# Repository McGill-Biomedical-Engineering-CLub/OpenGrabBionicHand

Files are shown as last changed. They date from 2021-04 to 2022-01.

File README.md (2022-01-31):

# OpenGrabBionicHand
### Date Launched: June 3, 2020
### Date Delivered: September 1, 2020
# Electronic Hardware System
## Circuit Schematic


### Parts Used:
* Arduino Pro Mini: Used to control all other electronics in the device. Receives analog input from the emg sensor and outputs commands to the servo shield and lcd screen via i2c communication. Datasheet: https://components101.com/microcontrollers/arduino-pro-mini
* FT231X: Provides the Arduino with serial communication from a USB port connected to the laptop. Datasheet: https://www.sparkfun.com/products/13263
* Gravity EMG Muscle Sensor: Measures the EMG signal at the patient's muscle and outputs a 10 bit ADC signal (range of 0-1023) to the analog pin A0 of the Arduino UNO. The device consists of 2 modules: The electrode module, containing 3 dry electrodes, is strapped to the user's muscle, and the signal processing module, which performs basic differential signal processing and interfaces with the analog pin. Datasheet: https://wiki.dfrobot.com/Analog_EMG_Sensor_by_OYMotion_SKU_SEN0240
* Servo Controller (PCA 9685): 16-channel servo controller. Receives power input from the external power supply and control input from the Arduino via I2C interface. Can control up to 16 servos using PWM signals (pulse with modulation). 
Datasheet: https://cdn-learn.adafruit.com/downloads/pdf/16-channel-pwm-servo-driver.pdf
* LCD Screen (SSD 1306): 0.96" 126x64 OLED screen. Displays to the patient calibration instructions. Communicates with the Arduino via I2C interface. Datasheet: https://components101.com/oled-display-ssd1306
* Rotational Servos (HS-65MG): 6V servo motor with 3 input pins (VCC, GND, PWM). Controlled by the servo controller. Datasheet: https://www.robotshop.com/en/hs-65mg-metal-gear-feather-micro-servo-motor.html
* Power Supply: 7.4V Rechargable LiPo Battery (2200 mAh). Datasheet: https://abra-electronics.com/batteries-holders/batteries-polymer-lithium-ion/prt-11856-polymer-lithium-ion-battery-2200mah-74v-prt-11856.html
### Soldering:
The modules for this circuit are connected on a 5x7cm soldering board. Both sides of the board are utilized to place the components. 


### Current Consumption
Non-Motor Components: (From Datasheets)
|Component |  Idle | Operational | Source of Measurement |  
| ------------- | ------------- | ------------- | ------------- |
|Arduino Pro Mini 5V | 3.1mA | 19.9mA | http://www.home-automation-community.com/arduino-low-power-how-to-run-atmega328p-for-a-year-on-coin-cell-battery/#:~:text=Using%20an%20Arduino%20Pro%20Mini,%2C%20in%20power%2Ddown%20sleep. |
| Gravity EMG Sensor | 0.5mA | 0.5 mA | Measured manually using INA219 current sensor |
| OLED Screen | 1.5mA | 4 mA | Measured manually using INA219 current sensor |
| Servo Controller | 2.2mA | 40mA | Datasheet: https://cdn-shop.adafruit.com/datasheets/PCA9685.pdf |
|**Total**|7.3mA |64.4mA| | 

Adding Motor Consumption

Using an INA 219 current sensor, the current consumed by the motors is measured. This measurement is done on 3 different states of the arm: Idle Open, Idle Closed, and a continous alternation between both states. With a known battery capacity of 2200mAh, the battery life can be calculated.

| Hand State |	Average Motor Current Consumption (mA)	| Average Total Current Consumption (mA)	| Estimated Battery Operating Time (hr) |
| ------------- | ------------- | ------------- | ------------- |
| Idle Open |	41	| 106	| 20.75 |
| Idle Closed	| 181	| 246	| 8.94 |
| Alternating	| 456	| **521**	| **4.22** |

Motor Current Consumption Profile


* It is important to note that only motor current consumption was measured and consumption by other modules are not taken into consideration for this measurement, as the motors are the main source of current drainage. 
# Software System
## Dependency Graph (Internal Modules Only)

### Modules involved:
* Bionic_Arm_Controller (main file): Controls the arm (receives EMG input and outputs signals to servo motors) by calling functions from other modules. 
* Arm_Settings: Contains all dynamic parameters that the user can change in the code.
* Arm_Calibration: Runs the calibration for the arm. Collects samples from both resting and active states of the muscle and determines the signal threshold needed to separate between open and closed hand states. 
* Arm_Servo: Handles the direct control of the servos and allows other modules depending on it to call simple methods such as 'open finger' and 'close finger'
* Arm_Demo: Uses functions from the Arm_Servo library to execute a pre-determined set of maneuvers with the arm.
* Arm_Screen: Handles display commands to the OLED screen.
* Arm_Sampler: Collects an EMG sample from the analog pin. Performs all signal analysis. Evaluates samples and outputs an open/close or error command.  
## Errors and Alerts: 
* Electrode Misplacement Error: The dry electrode is not firmly attached to its position which results in readings that are much higher than the normal range. This error is printed to the screen and persists until the electrode position is adjusted to a valid one. 
## Signal Processing:

Unlike that of the Myoware sensor, the signal obtained from the analog reading of the Gravity EMG sensor is raw. The hardware only uses differential denoising to remove the common noise among the electrodes. Thus, the need for software-based signal processing arises.
 
Example of Raw Signal

raw

Differentiating a contraction from the resting phase visually in this noisy signal is still possible. However, there must be a systematic way that the software can use to easily distinguish between both phases. Hence, a variety of techniques must be used:
1. Establishing a zero baseline: The raw signal has a resting-phase baseline that ranges between 280 and 350 units of amplitude (1 unit = 5V/1024). During calibration, the average value of this baseline is determined. Upon each subsequent reading, the absolute value of the difference between the raw reading and the baseline is calculated to obtain a 'normalized' signal reading.
2. Moving Average Filter: To obtain more smoothing of the signal and to mitigate the effect of sudden noisy spikes in measurements, a moving average filter of window width 8 is used. The filter was implemented internally (no use of external libraries) and by trial-and-error, the mentioned window width was found to be most convenient in terms of signal quality and memory usage. 
3. Multiplying factor: At the end, the processed signal readings are multiplied by a certain factor to make different readings more distinguishable from each other. A factor of 2 was chosen. It is worth mentioning that squaring the readings was an option that was considered; however, this method was found to require double the amount of memory, as it causes overflows in the 16 bit integers used to store the datapoints. 
4. Sampling Rate: The sampling rate also has an impact on the quality of the output signal. A rate of 50Hz is found to be convenient. 

Note: Frequency domain-based signal processing is not applicable to this iteration, as it requires a significant amount of memory. The Arduino Pro Mini total RAM memory is only 2048 Bytes, of which most are used for calibration and the LCD screen. 

Example of Processed Signal

final_sig

As seen in the figure above, clear peaks can be identified in the signal, with each peak corresponding to a muscle contraction.

## Calibration 
The function CalibrateDry is used mainly for this iteration. It is found in the Arm_Calibration.cpp file. 
### Determining the baseline
Before starting calibration, a baseline must be established in order to proceed with sampling. The user is instructed to relax and 100 EMG samples are taken at a rate of 100Hz. The average of those 100 samples is the obtained baseline. This value is then to be verified by the checkBelow function which tests the baseline value and ensures that 30 consecutive readings resting values lie below 50. If that is not the case, then the function responsible for updating the baseline is called again and the new baseline is validated. This process repeats until a valid baseline is obtained and tested. 
### Algorithm for Finding the Threshold Value
The same algorithm used from Iteration 1 (Advanced Calibration) is used to find the threshold value that sets apart the resting state from the contracting state. The only changes done are the following: 
* The control system for this iteration does not require 2 threshold values (high and low). Hence, only 1 threshold value to to be determined by the algorithm. 
* The new signal processing technique is used. All samples are obtained using the simpleSample function, as opposed to the first iteration where samples are directly obtained from AnalogRead. 
### Skip Calibration option
Because the full calibration process takes over 1 minute, the user has the option of skipping most of it. This option limits calibration to only establishing the baseline for each channel and assumes a default threshold of 12. With this option calibration would take around 3 seconds for 1 channel and 6 seconds for 2 channels.
## Sample Analysis and Control
The user is allowed to pre-select the number of EMG channels used to control the arm (1 or 2) by modifying the Arm_Settings.h file.
### 1 Channel Input
The control system used for this iteration consists of a toggle switch that is triggered by values above the threshold. Whenever 2 consecutive values are detected above the threshold value, the switch is activated and the state of the hand is changed. In other words, if the hand is open, the first contraction will cause it to close and the second contraction will cause it to open back again. Both contractions must be separated by a buffer refractory time of 800ms.  
The Arm_Sampler library also contains the tools used to judge whether the arm should be open or closed based on the obtained reading. The function evaluateSample returns an integer of either 0, 1, or 2 which correspond to the following:

0 -->Stay in the previous state

1 -->Change state (open if closed and close if open)

2 --> Electrode Misplacement Error (does not change state)

The following flow chart summarizes the control scheme for single channel input control:



### 2 Channel Input
The arm sampler first processes the incoming signal from each channel separately. Upon obtaining the 2 datapoints, the signal from the first (main) channel is evaluated. If a peak is detected, then the hand will immediately be ordered to the open position if closed, and to the close position if in any other position. This is similar to what occurs in 1-channel input control.
If no peak is detected from the first channel, then the device 'listens' to the processed input from the second channel. If a peak is detected from the second channel, then a 3rd 'special' position is performed by the hand. If no peak is detected from either channel, the hand remains in its previous state.
The function evaluateSample2Electrodes handles control for the 2 channel input option. The function returns the following possible outputs:

0 -->Stay in the previous state

1 -->Change state (open if closed and close if in other position)

2 --> Electrode Misplacement Error (does not change state)

3 --> Perform special movement

The following flow chart summarizes the control scheme for 2 channel input control:



# Testing
## Preliminary Testing
Testing was done on 3 usage cycles (calibrate-operate-reset). The primary electrode was placed on the biceps muscle whereas the secondary electrode was placed on the Brachio Radialis muscle.
Testing with PLA skin: 
| Test | Round 1 | Round 2| Round 3 |
| ------------- | ------------- | ------------- | ------------- | 
| Resting Hand False Positives |    0   | 0  | 0 |
| Moving Elbow False Positives |   0 |   0|  0|
| Tapping Hand False Positives |    1  |   2 |1  |
| 10 Contractions | 10/10 |  10/10 | 10/10 |
| 10 Special Movement | 10/10 | 10 /10 | 10/10 |
| 10 Contractions with hold | 10/10 | 10/10  | 10/10 |
| Glass Cup Test (small glass)| 10/10|  10/10 | 10/10 |
| Glass Cup Test (large glass)| 0/10|  0/10 | 0/10 |
| Apple Test | 5/10 | 6/10 | 8/10 |
Testing with Rubber Skin
| Test | Round 1 | Round 2| Round 3 |
| ------------- | ------------- | ------------- | ------------- | 
| Resting Hand False Positives |    0   | 0  | 0 |
| Moving Elbow False Positives |   1 |   0|  0|
| Tapping Hand False Positives |    1  |   1 |1  |
| 10 Contractions | 10/10 |  10/10 | 10/10 |
| 10 Special Movement | 10/10 | 10 /10 | 10/10 |
| 10 Contractions with hold | 10/10 | 10/10  | 10/10 |
| Glass Cup Test (small glass)| 10/10|  10/10 | 10/10 |
| Glass Cup Test (large glass)| 9/10|  10/10 | 10/10 |
| Apple Test | 10/10 | 10/10 | 10/10 |
### Test Protocol Details
Prior to each test: Install the Gravity EMG electrode on the Flexor Carpi Radialis Muscle location. Start the hand and calibrate it.

Resting Hand False Positives: Remain at rest for 1 minute. Report the number of movements initiated from false positive readings.

Moving Elbow False Positives: Similar procedure to Resting Hand False Positive Test. This test involves continously rotating the elbow slowly and reporting any false positives that occur within a minute.

Tapping Hand False Positives: Similar procedure to Resting Hand False Positive. This test involves gently tapping the hand at locations ~3cm away from the electrode in a continous manner and reporting false positives within a minute. 

10 Contractions: Perform 10 distinct contractions using the Flexor Carpi Radialis Muscle, once every 10 seconds. Report the number of successful hand movement responses to the muscle contractions.

10 Special Movements: Before starting the device, add a second electrode on the Biceps Radii Muscle and change the electrode number setting to 2 in the settings.h file. Perform 10 distinct contractions using the Biceps Radii Muscle, once every 10 seconds. Report the number of successful special hand movement responses to the muscle contractions.

10 Contractions with hold: Same protocol as the 10 Contractions test. Leave 30 seconds between 2 successive contractions. 

Glass Cup Tests: Use the hand to pick up an empty glass cup, move it along a distance of 50cm, then lay it down at a specific target point. A glass cup weighing ~200g is used for the small glass and a cup weighing ~500g is used for the large glass. Perform this task 10 times and record the number of successful attempts.

Apple Test: Use the hand to pick up an average size McIntosh Apple, move it along a horizontal distance of 50cm, then place it down on a target location. Perform this task 10 times and record the number of successful attempts.

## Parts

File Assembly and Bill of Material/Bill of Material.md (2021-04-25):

# Bill of Material
| Item | Quantity | Unit |Cost per unit ($CAD)| Cost ($CAD)|Notes
| ------------- | ------------- | ------------- | ------------- | ------------- | ------------- | 
|3D printing Filament for PLA|	1|	per kg|	32.00|	32.00	|All the 3D components are included here.|
|7.4V Rechargable LiPo Battery| 	1|	each|	20.00|	20.00|	
|Wires ||||4.00|	Sufficently large quantities of soldering wire.|
|Soldering Board|	1|	each|	0.40|	0.40||	
|Arduino Pro Mini	|1|	each|	5.00|	5.00||
|USB interface for Arduino mini (FT231X)|	1|	each|	13.00|	13.00|	|
|LCD Monochrome 0.96” OLED Display (SSD1306)|	1|each|	7.00|	7.00||
|HS-65MG Servo Motor	|5	|each	|27.00	|135.00	||
|Servo Controller (PCA 9685)|	1|	each|	16.00|	16.00||	
|SEN0240 Gravity: Analog EMG Sensor	|2	|each	|75.00	|150.00|	Maximal estimate.|
|M3 nuts|1	|pack of 25	|1.50	|1.50	|
|M3 Brass Heat Inserts (4.90mmx4mm)|	1|	pack of 10|	1.10|	1.10||	
|M3x15mm screws	|1|	pack of 10|	2.00|	2.00	||
|M3x4mm screws	|1	|pack of 10	|2.00	|2.00	||
|M3x5mm screws	|1	|pack of 10	|2.00	|2.00	||
|5.25mm ID Shaft Retention Bushing Lock	|5|	each|	1.10|	5.50	|ID: Internal diameter. Must be larger than servo horn diameter(>5mm)|
|Fishing Line (>20 lbs)	|1	|300m-450m of wire	|20.00	|20.00|	Spool quantity to the discretion of the buyer.|
|**Total**	 |||||	 	 **384.50**	 ||

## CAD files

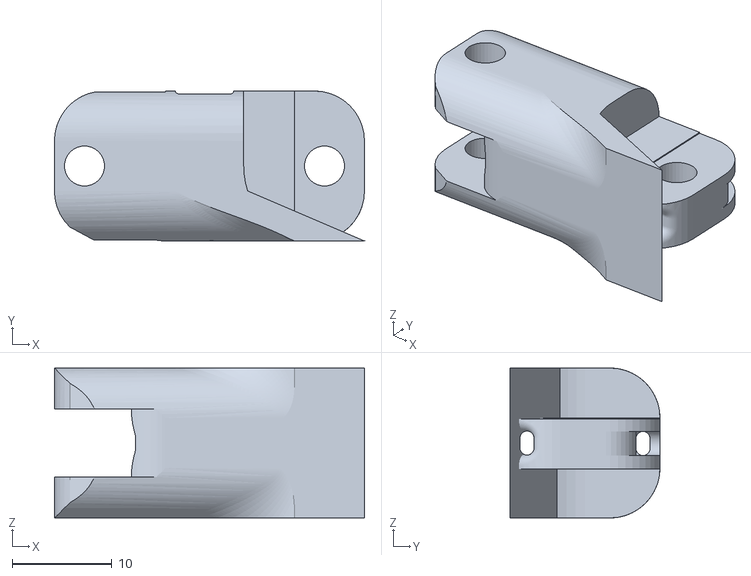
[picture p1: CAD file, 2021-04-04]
3D Print Files/Pinkie finger 3.3 Proximal (Zip).STL
31.0 x 15.0 x 15.0

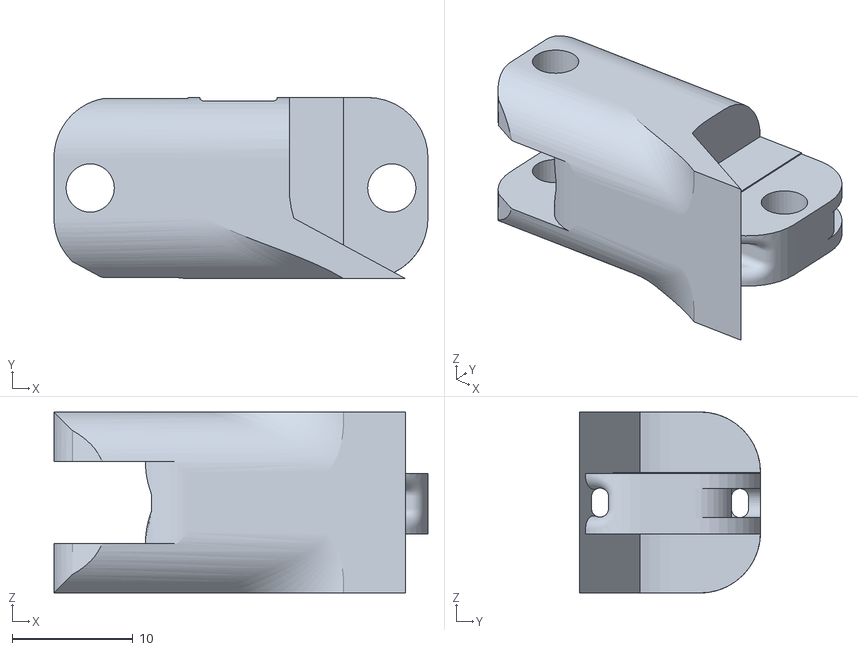
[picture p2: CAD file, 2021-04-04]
3D Print Files/Pinkie finger 3.3 Middle (Zip).STL
31.0 x 15.0 x 15.0

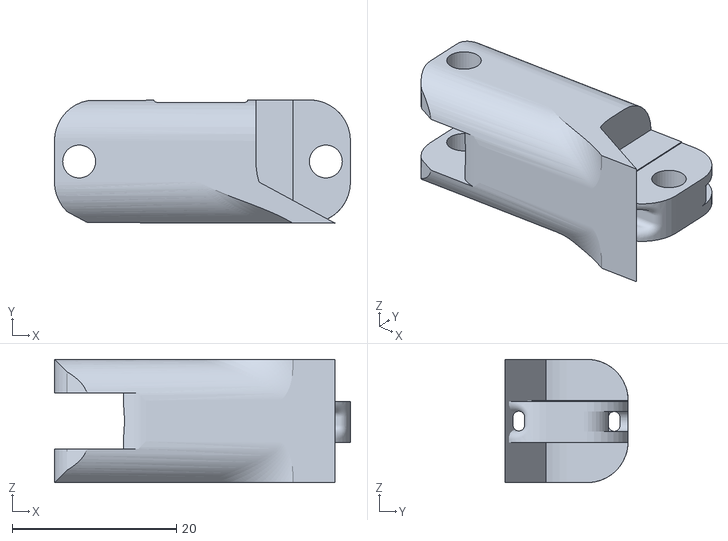
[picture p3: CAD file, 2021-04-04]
3D Print Files/Index-Ring finger Middle 3.3 (Zip).STL
36.0 x 15.0 x 15.0

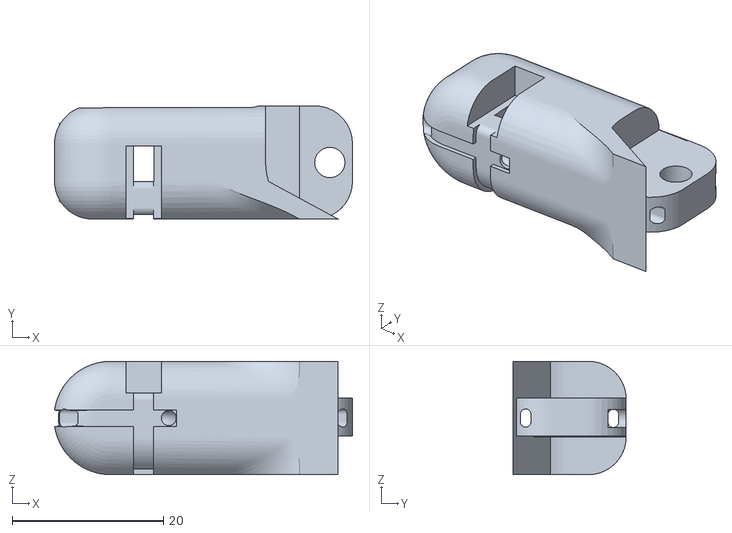
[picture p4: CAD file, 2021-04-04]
3D Print Files/Index-Ring finger Distal 3.4 (Zip).STL
39.4 x 15.0 x 15.0

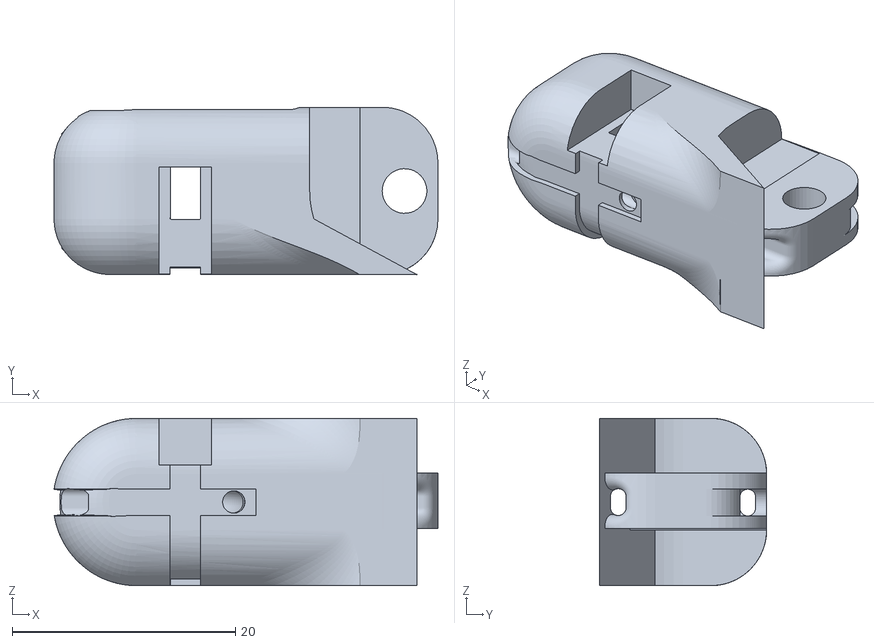
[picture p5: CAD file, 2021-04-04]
3D Print Files/Pinkie finger 3.4 Distal (Zip).STL
34.4 x 15.0 x 15.0

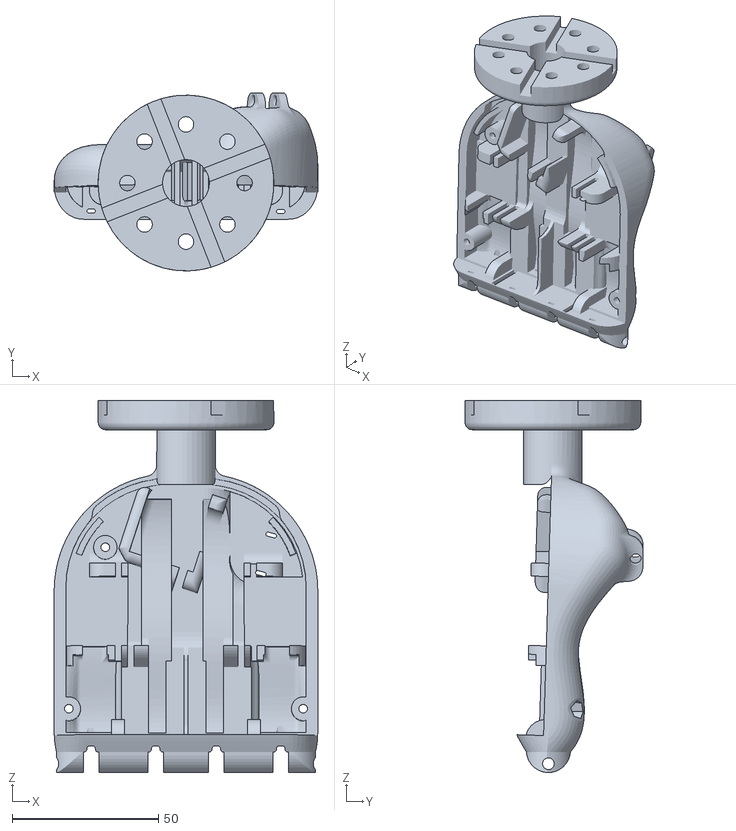
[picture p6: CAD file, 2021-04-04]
3D Print Files/Frontal Palm 1.8(HS-65mg+mg90s thumb).STL
90.0 x 60.7 x 127.0

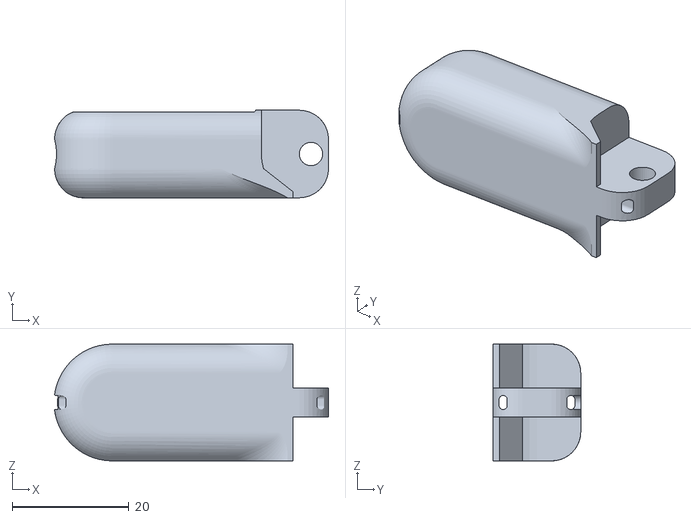
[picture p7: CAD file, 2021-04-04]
3D Print Files/Thumb finger 3.5 (Zip)- distal.STL
46.9 x 15.0 x 20.0

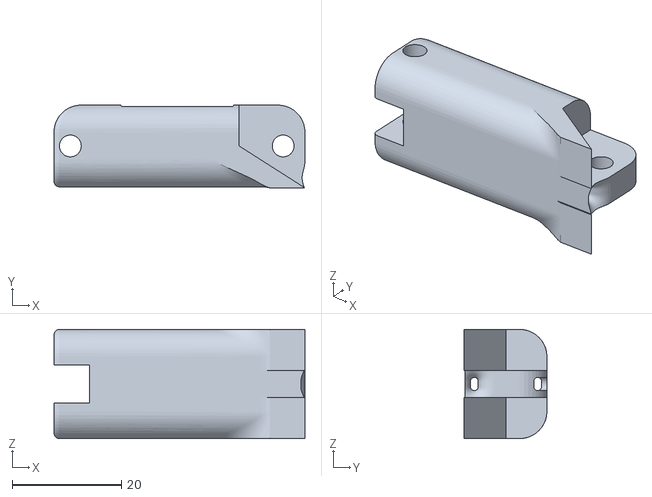
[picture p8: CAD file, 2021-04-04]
3D Print Files/Thumb finger 3.5 (Zip)- proximal.STL
46.0 x 15.2 x 20.0

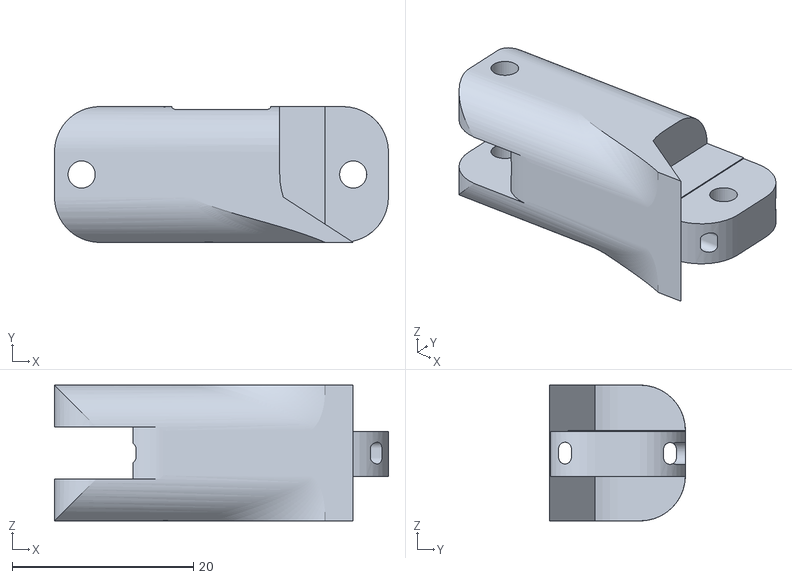
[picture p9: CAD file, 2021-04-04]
3D Print Files/Middle finger 3.4 Middle.STL
36.9 x 15.0 x 15.0

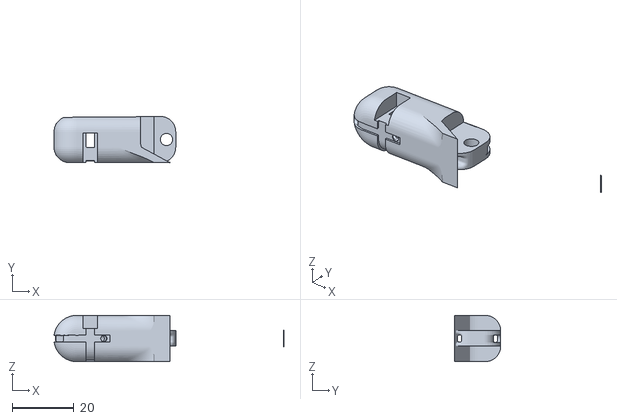
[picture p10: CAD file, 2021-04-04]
3D Print Files/Middle finger 3.4 Distal(Zip).STL
74.5 x 15.0 x 15.0

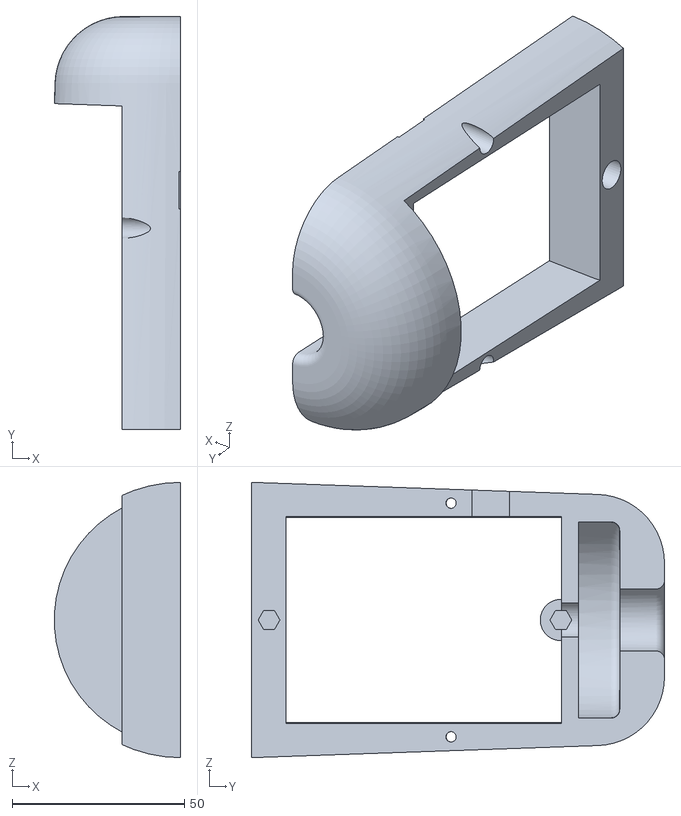
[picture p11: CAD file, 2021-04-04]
3D Print Files/Forearm 3.5-Dorsal forearm.STL
36.6 x 120.0 x 80.0

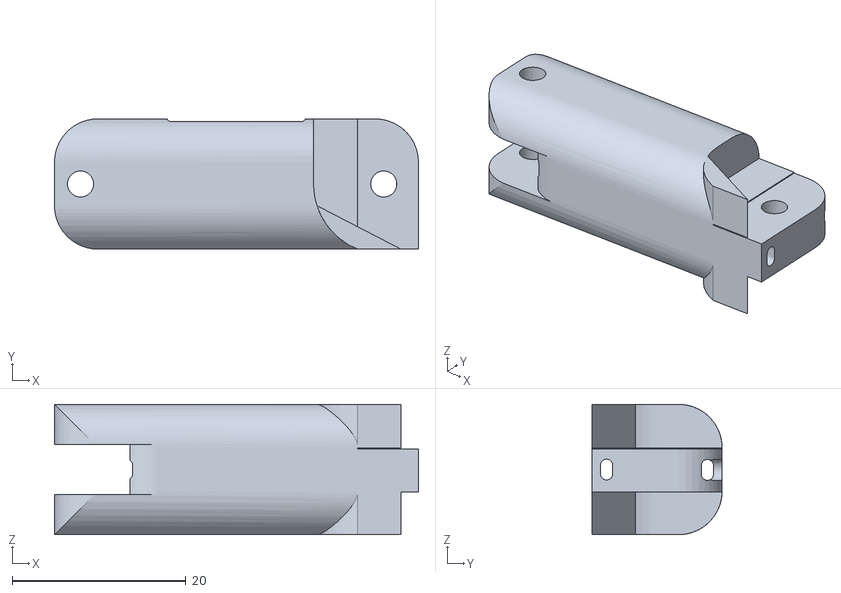
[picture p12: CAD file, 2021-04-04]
3D Print Files/Middle finger 3.4 Proximal.STL
41.9 x 15.0 x 15.0

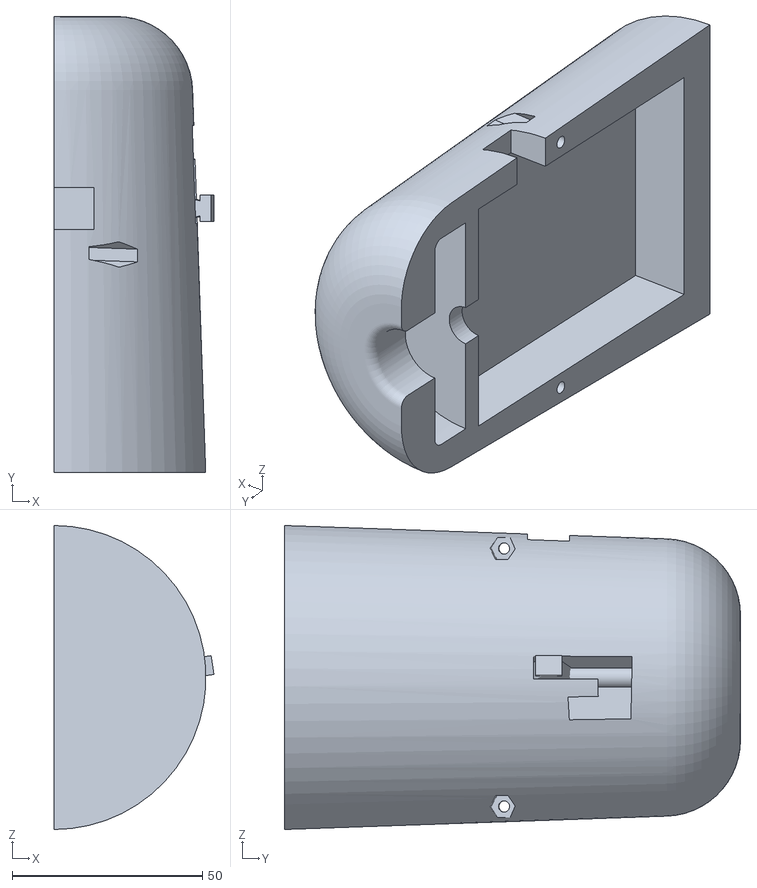
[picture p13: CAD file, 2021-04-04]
3D Print Files/Forearm 3.5- Palmar forearm.STL
42.1 x 120.0 x 80.0

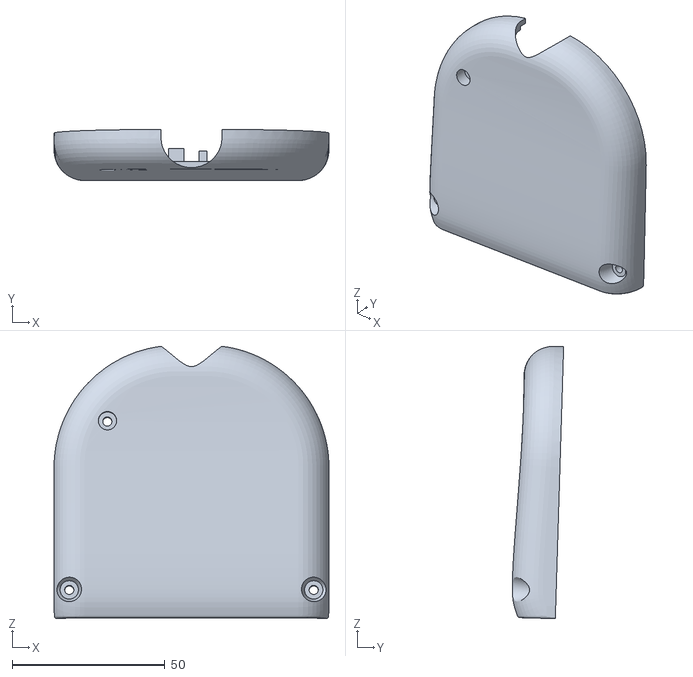
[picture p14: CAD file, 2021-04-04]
3D Print Files/Dorsal Palm 1.8(HS-65mg+mg90s thumb).STL
90.0 x 16.8 x 89.2

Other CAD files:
3D Print Files/Index-Ring finger Proximal 3.3 (Zip).STL
3D Print Files/3mm nail.STL
3D Print Files/Forearm 3.5-Electronics Cover.STL
3D Print Files/3mm palm nail.STL
3D Print Files/Screw Spool 2.4.2 (18mm).STL

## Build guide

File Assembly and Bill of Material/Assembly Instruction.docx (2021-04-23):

Item No. | Part Name | Description | Qty.
1 | Frontal Palm | | 1
2 | Dorsal Palm | | 1
3 | Forearm Dorsal | Includes a non-removable locking mechanism | 1
4 | Forearm Frontal | | 1
5 | Forearm Electronic Cover | | 1
6 | Hitec HS-65MG Servo Motor | | 5
7 | Phalange Pinkie Distal | | 1
8 | Phalange Pinkie Medial | | 1
9 | Phalange Pinkie Proximal | | 1
10 | Phalange Middle Distal | | 1
11 | Phalange Middle Medial | | 1
12 | Phalange Middle Proximal | | 1
13 | Phalange Index/Ring Distal | Index and ring finger share the same dimensions | 2
14 | Phalange Index/Ring Medial | | 2
15 | Phalange Index/Ring Proximal | | 2
16 | Phalange Thumb Distal | | 1
17 | Phalange Thumb Proximal | | 1
18 | Palm Dowel | | 1
19 | Finger Dowel | | 9
20 | Thumb Dowel | The thumb-palm connecting dowel is a Finger Dowel | 1
21 | Spool | | 5
22 | Servo Horn Retention Bushing Lock | | 5
23 | M3x4mm Screw | | 5
24 | M3x5mm Screw | | 5
25 | M3x15mm Screw | | 7
26 | M3 Nut | | 7
27 | M3x5mm Brass Insert | | 5
28 | M3 Allen key | | 1
29 | Fishing line (~50-70cm of length) | | 5

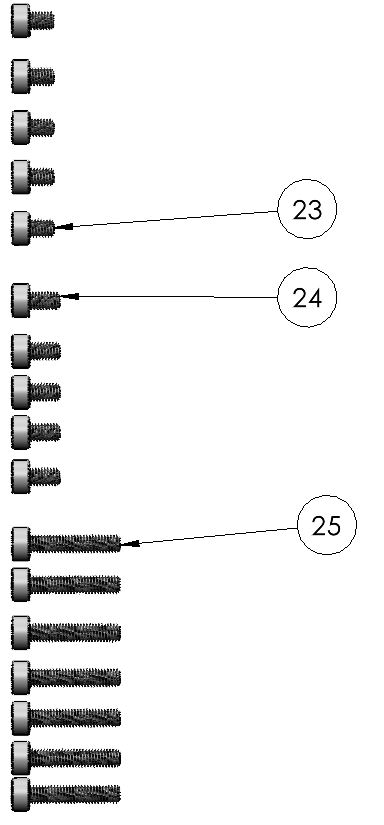
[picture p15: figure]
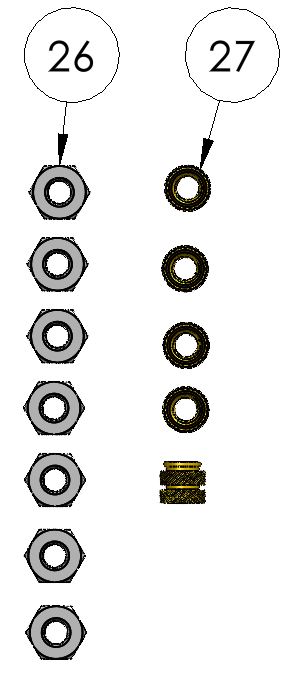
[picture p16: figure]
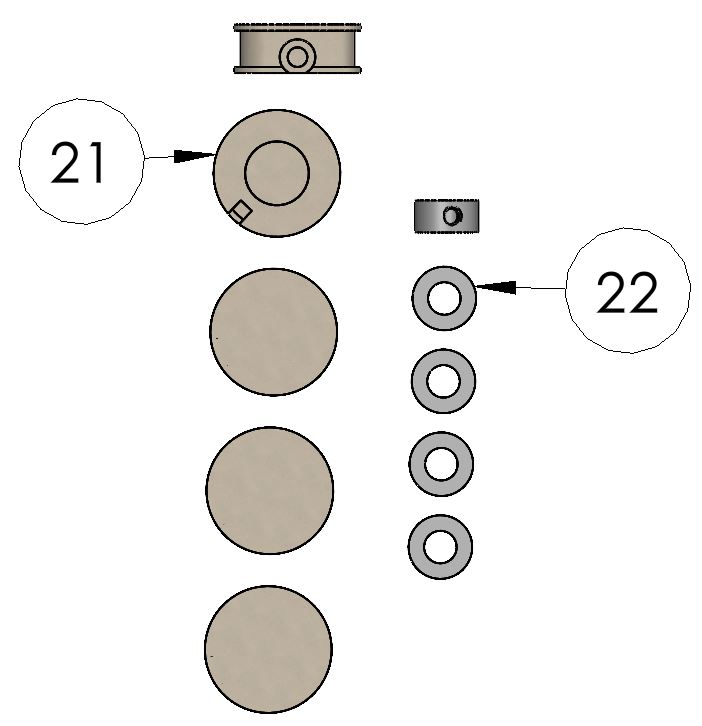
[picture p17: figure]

Assembly Steps

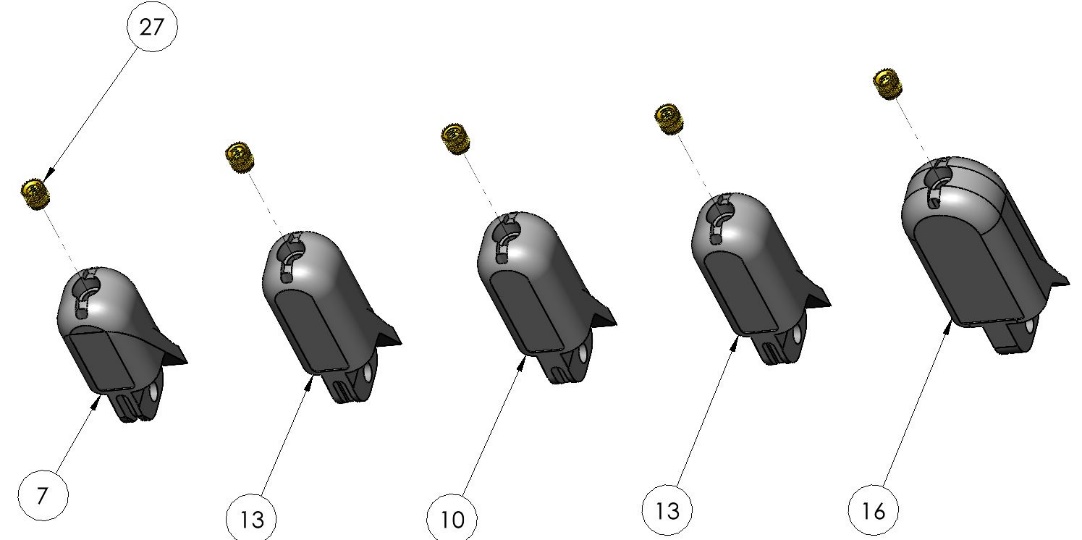
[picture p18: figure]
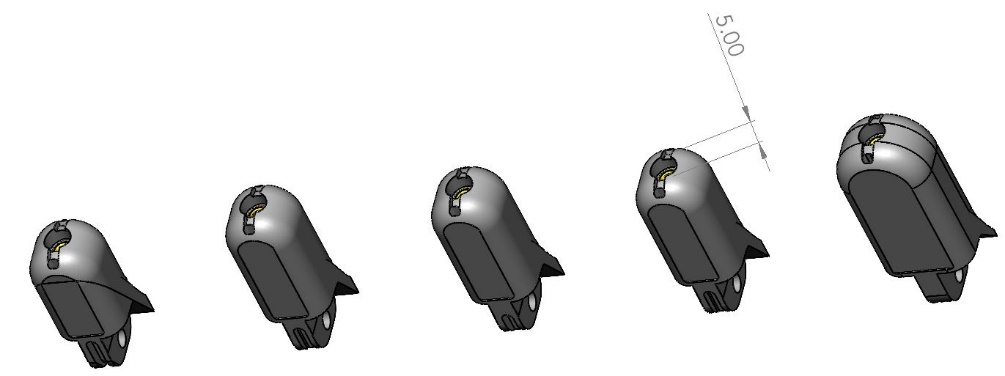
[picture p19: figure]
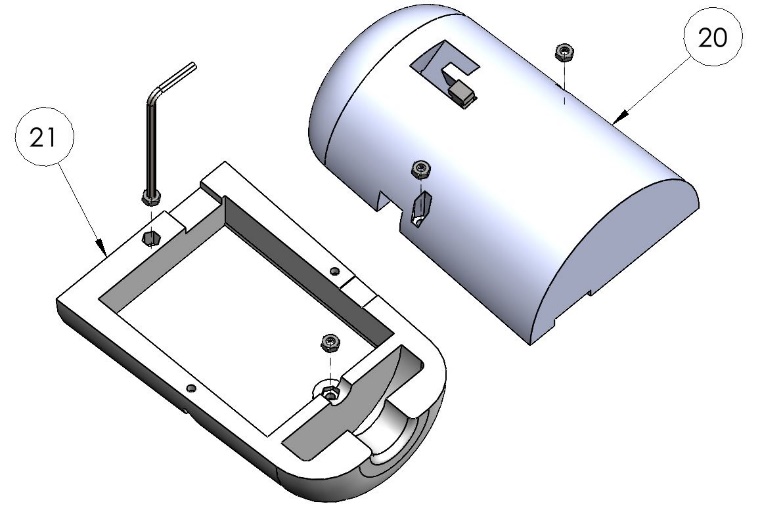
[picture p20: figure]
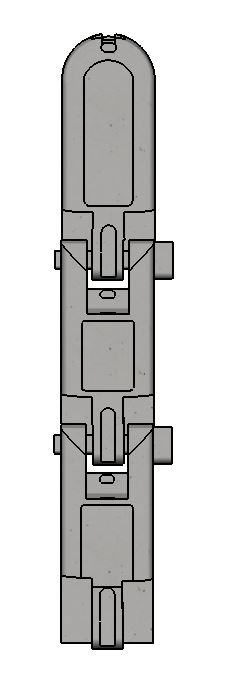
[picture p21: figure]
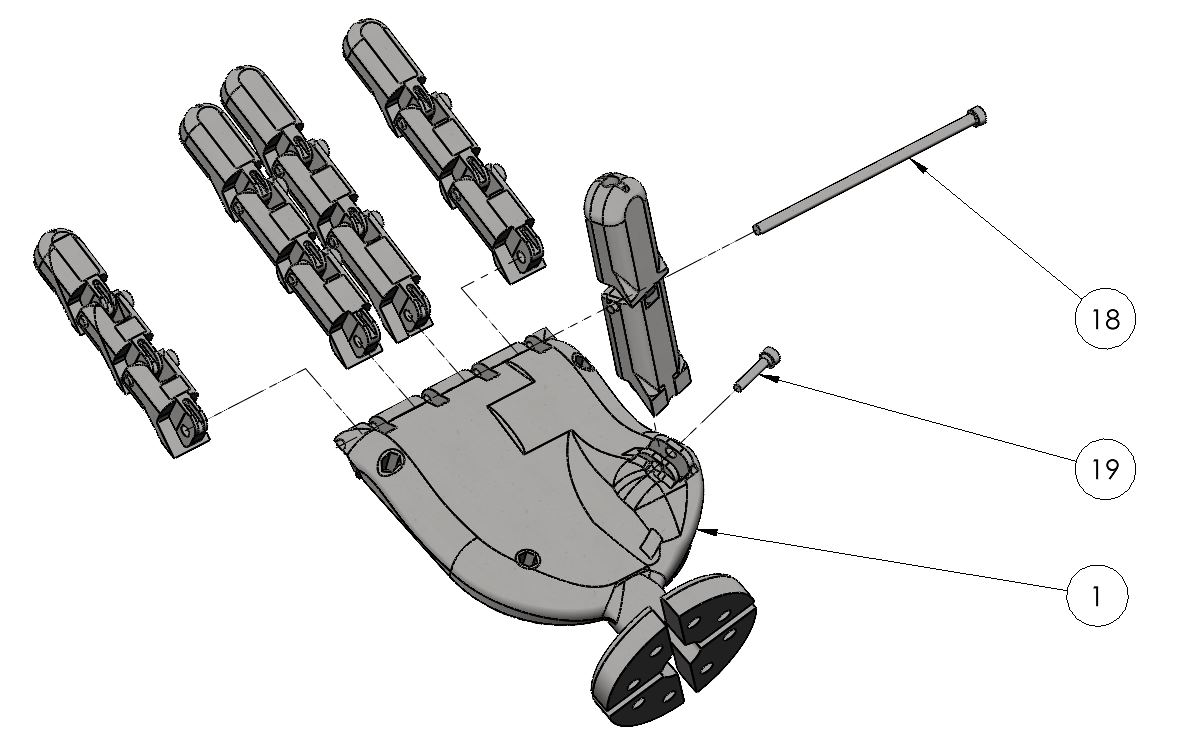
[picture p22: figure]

Make sure to repeat the previous steps for the other fingers before inserting the palm dowel (18).

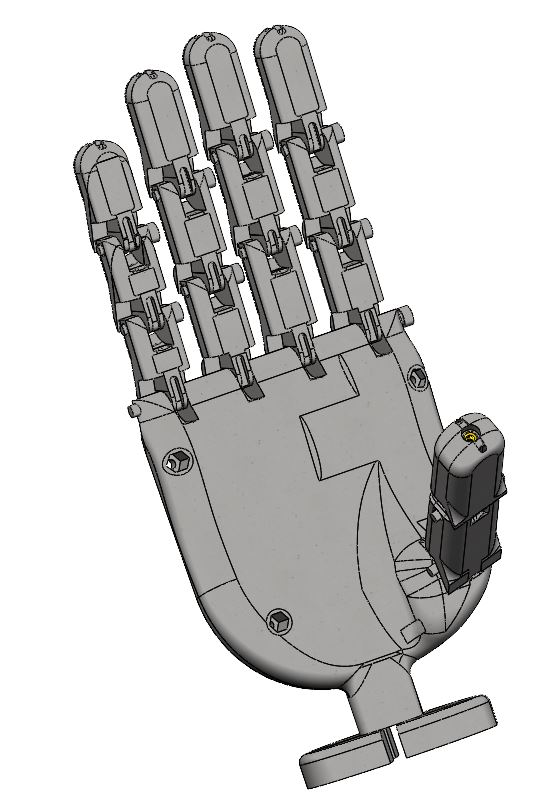
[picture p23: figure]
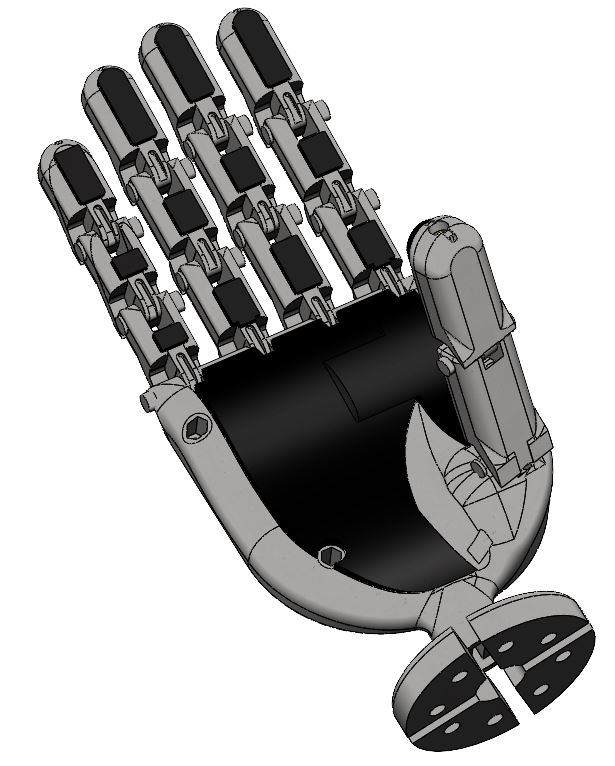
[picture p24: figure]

Apply rubber pads (shown in black)

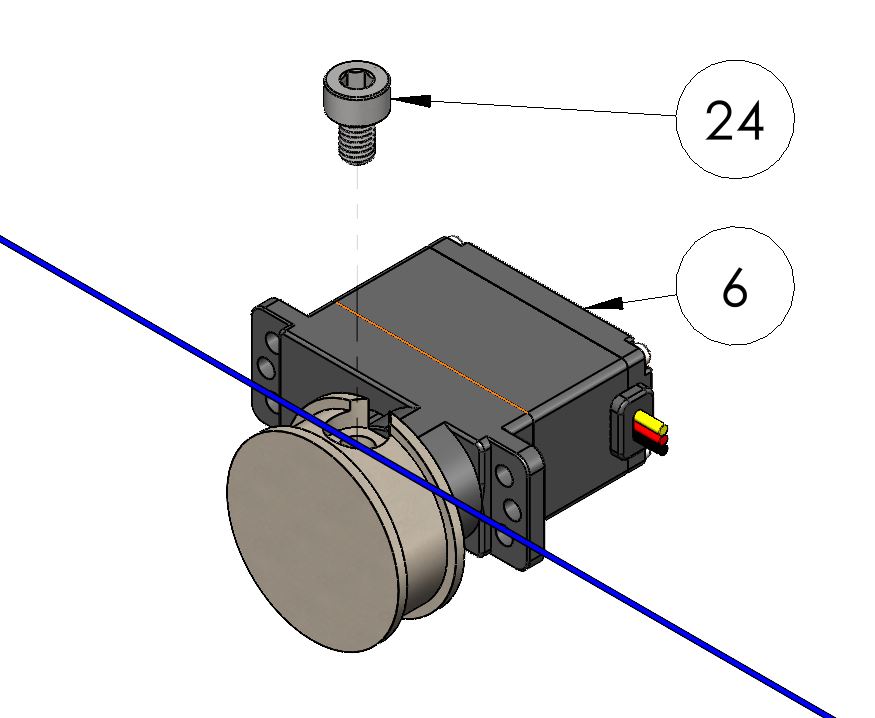
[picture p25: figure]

Repeat for each motor.

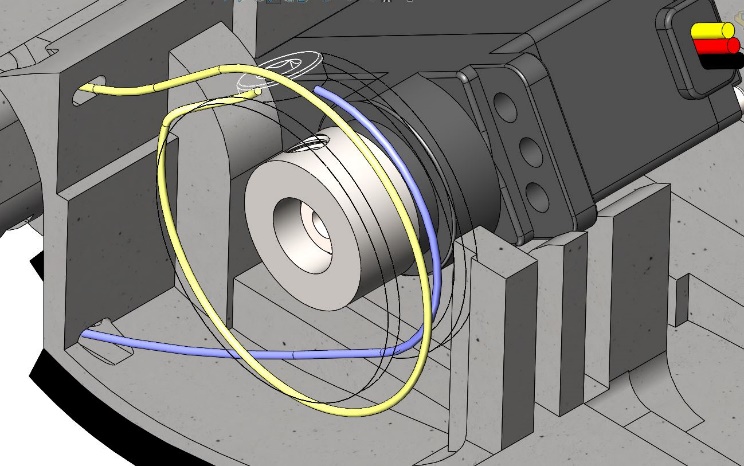
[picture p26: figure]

Cross-sectional view

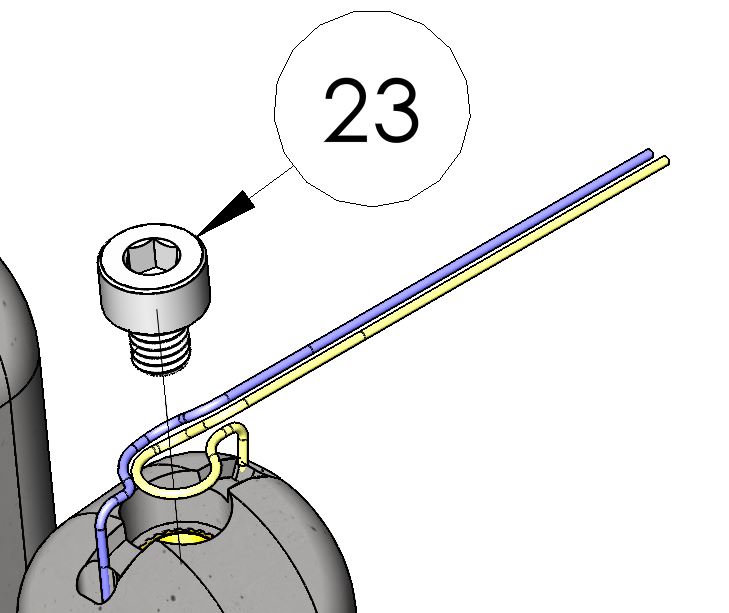
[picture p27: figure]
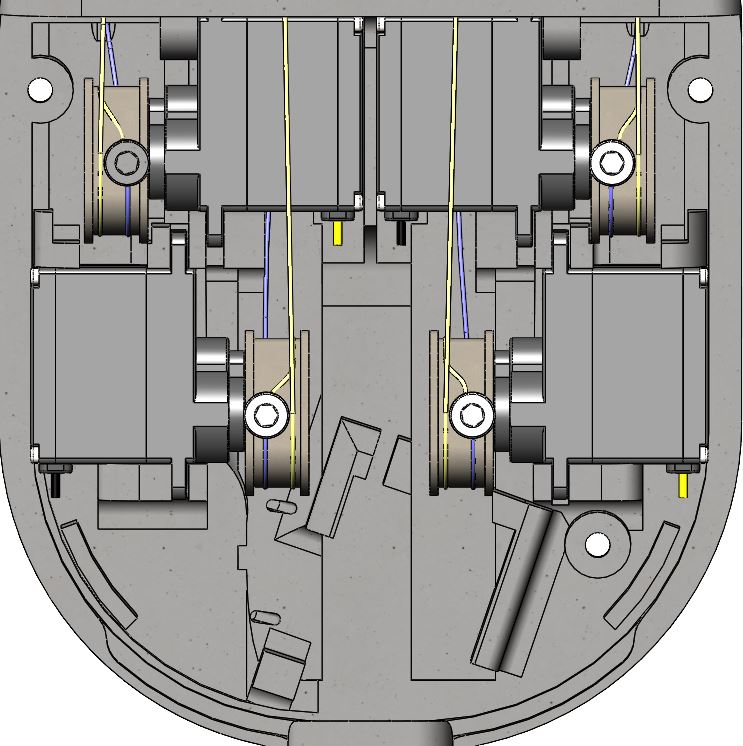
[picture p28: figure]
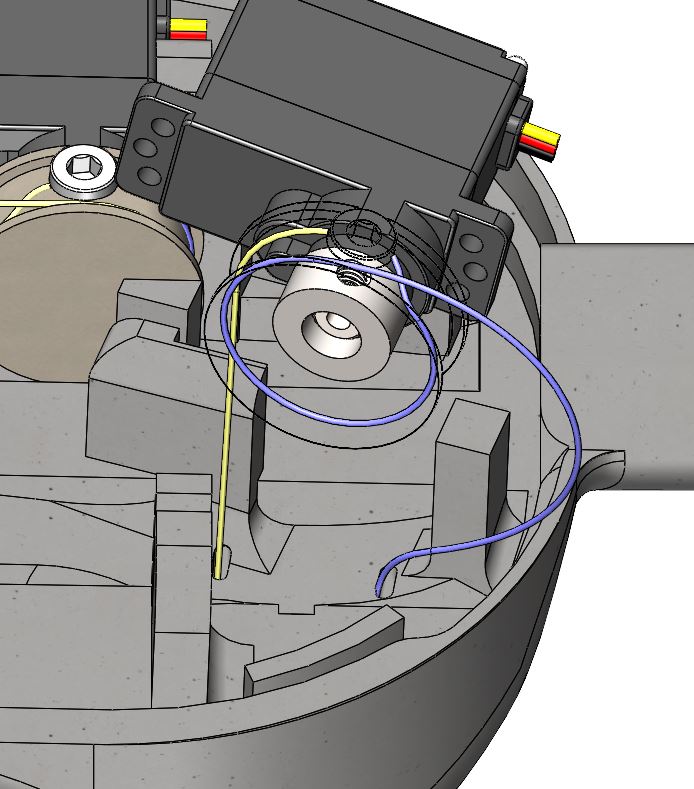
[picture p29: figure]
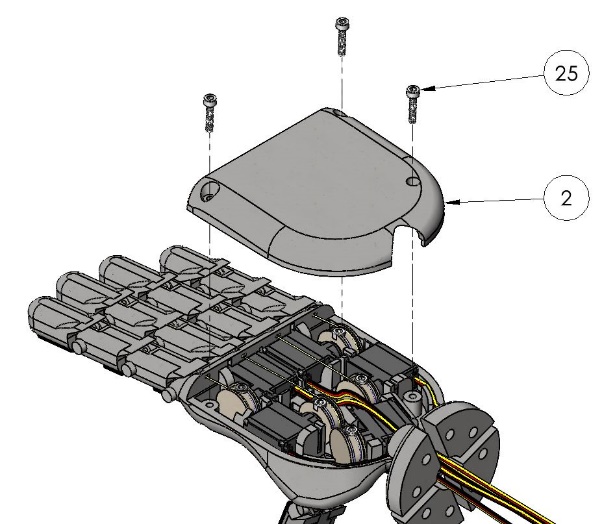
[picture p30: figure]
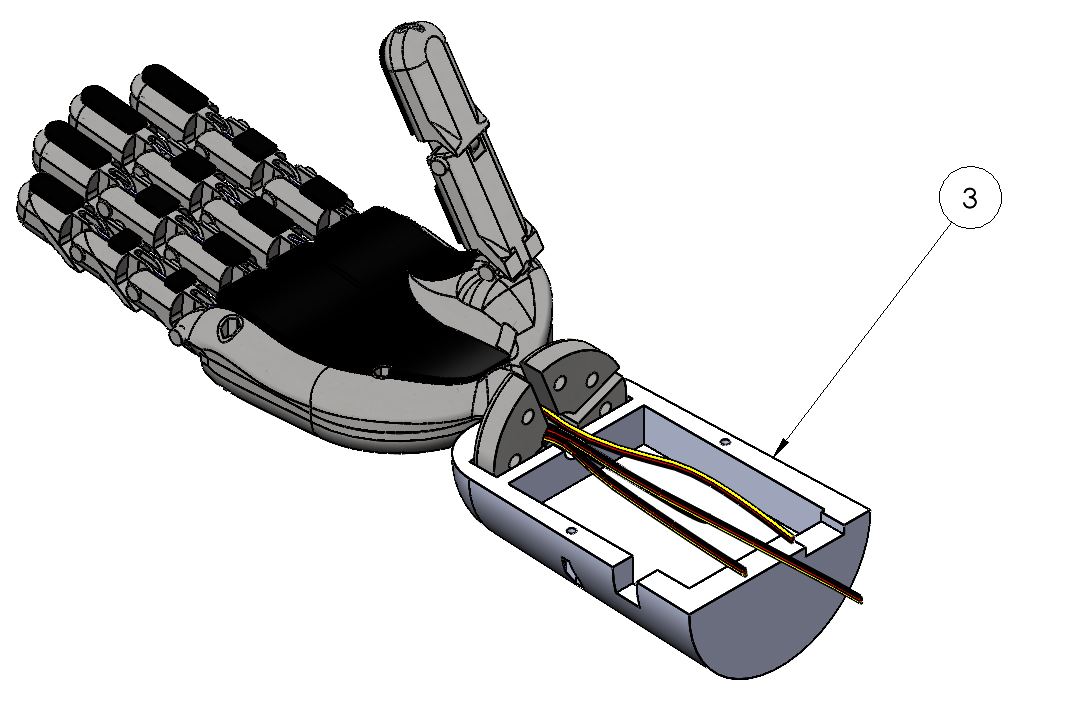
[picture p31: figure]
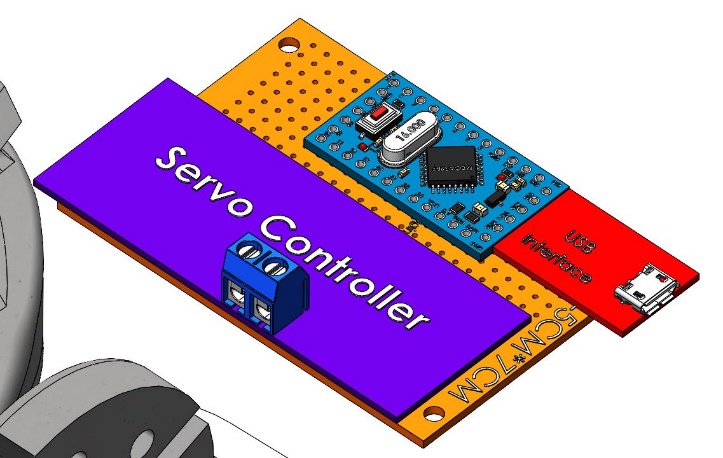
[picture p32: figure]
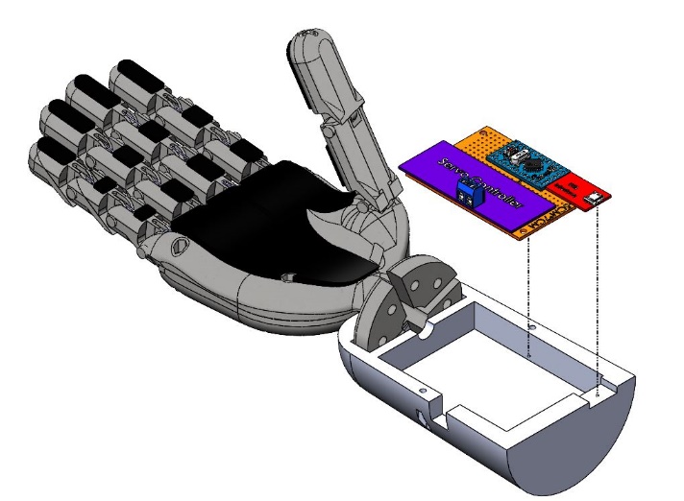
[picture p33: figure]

For Clarity, the servo cable was hidden, but refer to the electronic schematic on how to connect each component.

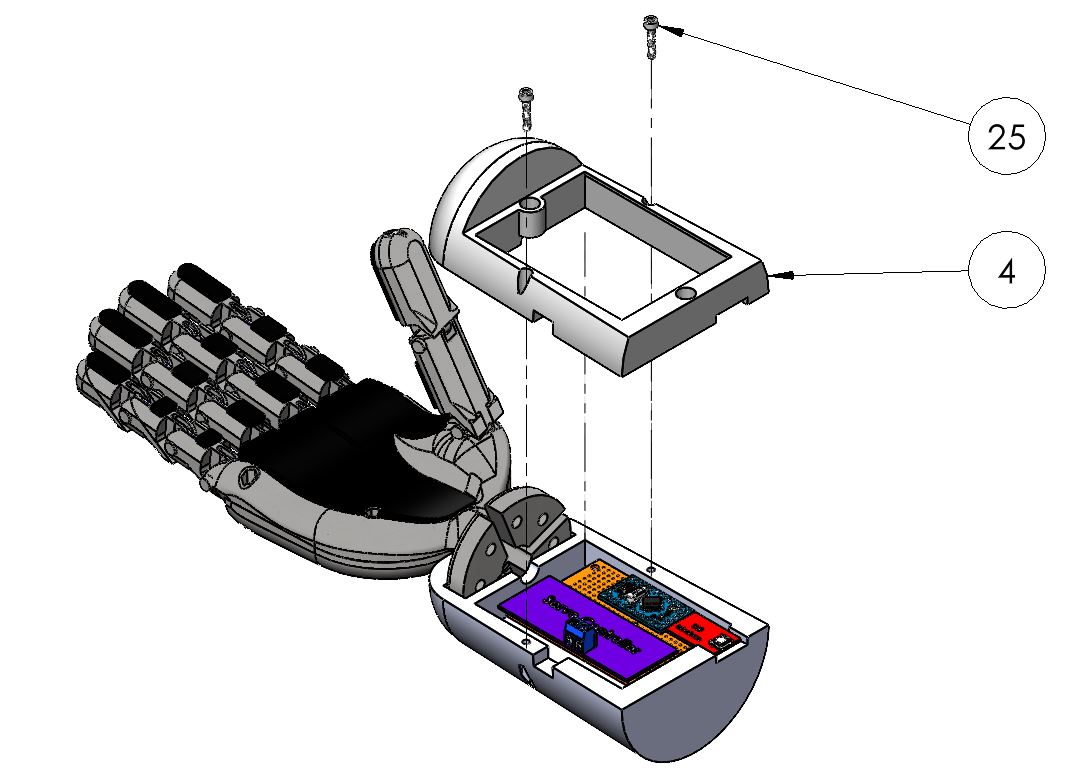
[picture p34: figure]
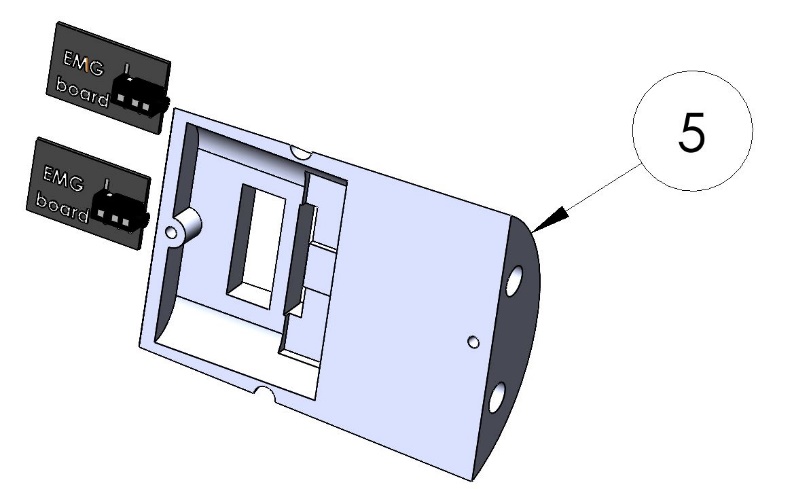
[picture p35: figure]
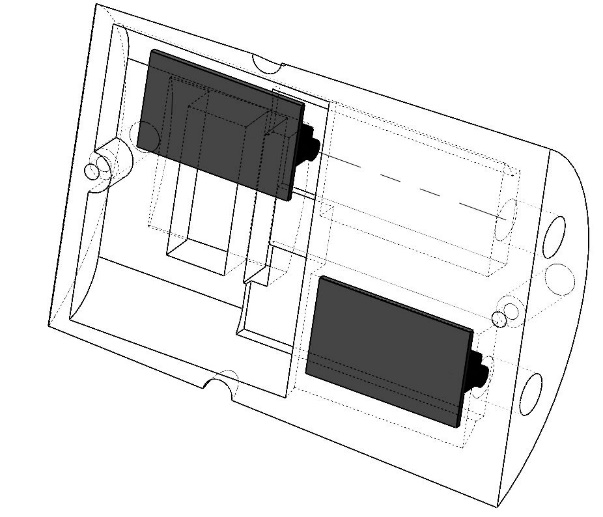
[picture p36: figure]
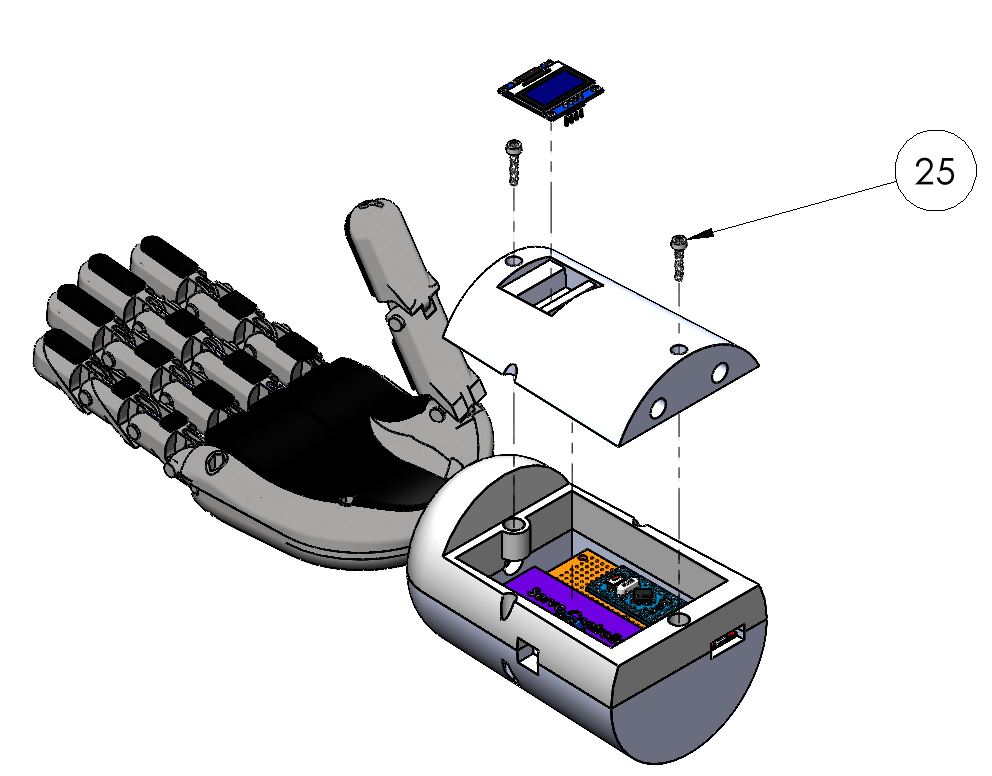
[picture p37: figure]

The LCD Screen’s steel wire male port should connect into the female connecting port located on top of the electronic board. See electronic schematic on how to connect.

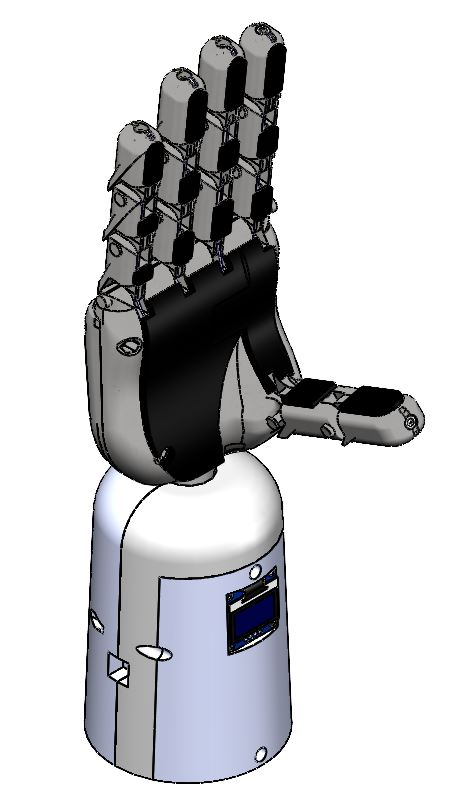
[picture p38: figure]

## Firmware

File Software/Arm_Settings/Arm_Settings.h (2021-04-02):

/*
  Author: Abdullatif Hassan <abdullatif.hassan@mail.mcgill.ca>
  Source Repository: https://github.com/Abdul099/Bionic-Arm-Controller
  Last Updated: August 24, 2020
*/

#ifndef Arm_Settings_h
#define Arm_Settings_h

//#define BRUNEL_ARM
#define MBEC_ARM

#define SKIP_CALIBRATION 1
#define LED_DEBUG_MODE 0
#define SPECIAL_POSITION 2

//emg channel and servo settings
#define NUM_CHANNELS 2 //1 or 2
#define NUM_SERVOS 5//max 5
#define emgpin1 A0
#define emgpin2 A3
#define indexServo 3//pin on servo relay module
#define thumbServo 0
#define middleServo 1 
#define ringServo 2
#define pinkyServo 4


#ifdef BRUNEL_ARM
#define HAND_TYPE 0
#define PWM_frequency 60
#define SERVOMIN 230 
#define SERVOMAX 410 
#define THUMB_MOD 25 //20
#define INDEX_MOD 20  //20
#define MIDDLE_MOD 20 //25
#define RING_MOD 50 //30
#define PINKY_MOD 0 //not used in this case but must be defined nevertheless
#define THUMB_MIN 300
#define INDEX_MIN 230
#define MIDDLE_MIN 230
#define RING_MIN 230
#define PINKY_MIN 230
#define THUMB_MAX 410
#define INDEX_MAX 430
#define MIDDLE_MAX 410
#define RING_MAX 475
#define PINKY_MAX 410
#define THUMB_MID 300
#define MIDDLE_MID 300
#endif

#ifdef MBEC_ARM
#define HAND_TYPE 1
#define PWM_frequency 50
#define SERVOMIN 610
#define SERVOMAX 2360
#define THUMB_MOD 0 
#define INDEX_MOD 0
#define MIDDLE_MOD 0
#define RING_MOD 0
#define PINKY_MOD 0
//closed
#define THUMB_MIN 320
#define INDEX_MIN 170//170
#define MIDDLE_MIN 400//400
#define RING_MIN 180//440
#define PINKY_MIN 430//155
//open
#define THUMB_MAX 170
#define INDEX_MAX 450//455
#define MIDDLE_MAX 133//133
#define RING_MAX 440//180
#define PINKY_MAX 210//440
//for special positions
#define THUMB_MID 300
#define MIDDLE_MID 300
#endif

//delay intervals
#define OPEN_DELAY 20
#define CLOSED_DELAY 20

//lcd screen settings
#define SCREEN_WIDTH 128
#define SCREEN_HEIGHT 64
#define OLED_RESET 13

//Calibration Settings
#define samples 200
#define NUM_CONTRACTIONS 10 // number of contractions needed for advanced calibration mode
#define SIZE_TRAININGDATA 30 //max 40
#define TRAINING_DELAY 20 //sampling period for trainingData

//sampler settings
#define THRESHOLD_TOLERENCE 2 //number of successive highs required to initiate a 'close hand' order
#define THRESHOLD_TOLERENCE2 2 //number of successive lows required to initiate an 'open hand' order
#define HOLD 2
#define buffer_arrayLength 8
#define PEAKWINDOW 10//20
#define PEAK_HOLD 0

#endif

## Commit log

2021-04-23 Create Bill of Material.md
2021-04-23 Update Bill of Material.md
